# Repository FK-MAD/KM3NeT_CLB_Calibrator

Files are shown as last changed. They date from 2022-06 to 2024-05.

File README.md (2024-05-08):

# KM3NeT CLB Calibrator
## About the KM3NeT CLB Calibrator
The KM3NeT CLB Calibrator is a mechanism that automatically calibrates the magnetic compass of the central logic boards (CLBs) used in the digital optical modules (DOMs) of the [KM3NeT](https://www.km3net.org) neutrino telescope. I designed and implemented the system during my internship at [N.C.S.R. “DEMOKRITOS” - Institute of Nuclear & Particle Physics](http://www.inp.demokritos.gr) between July and September 2020.

## Motivation
Every DOM of the KM3NeT telescope is submerged near the bottom of the Mediterranean Sea and continually reports its orientation based on data from the magnetic compass located on its CLB. For the magnetic compass to work properly, a calibration routine must be carried out for every CLB before its DOM integration. Conventionally, this is done manually using a gyroscope-like tool, seen below.

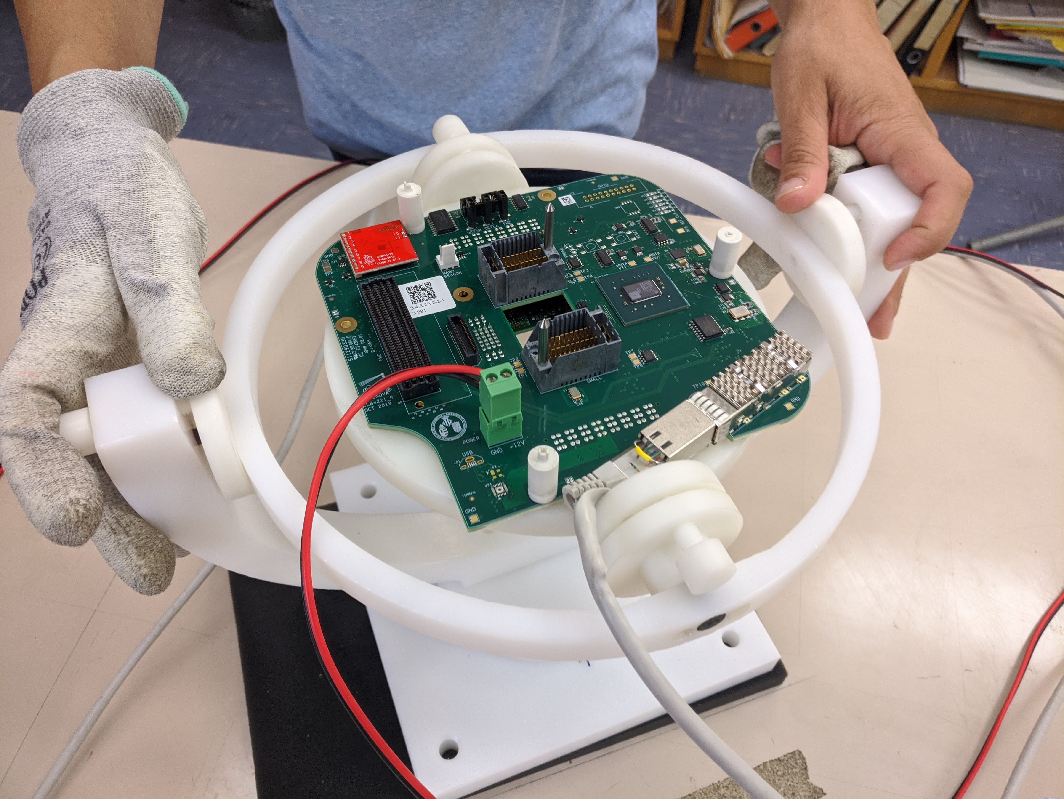
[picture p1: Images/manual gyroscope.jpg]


This process is monotonous, tedious and provides inconsistent calibration accuracy. For these reasons, an automated system needed to be developed.

## Design Constraints
The design constraints that the automated system needed to satisfy were the following.
1) No metal parts should exist near the CLB. This was to ensure that no interference occured with the earth's magnetic field during calibration.
2) The mechanism must perform a series of eight full 360° rotations about the vertical axis each one with the CLB placed in a different orientation.
3) Each rotation must be smooth and last approximately 20s to ensure good data acquisition.

## Calibrator design
The mechanism is composed of two sub-assemblies.
1) A: a gyroscope-like mechanism that rotates the CLB. It is made entirely out of plastic parts to satisfy design constraint #1. Most parts are 3D printed, some are machined in a lathe, while some are standard plastic bolts, nuts and timing belts.
2) B: a base for the stepper motors and other electronics located ~1 meter away from the CLB. Actuation between the stepper motors and the gyroscope-like mechanism is achieved using 3 long non-metalic timing belts.

Both sub-assemblies are secured on a wooden base with plastic bolts and nuts. The two sub-assemblies are seen below.



## Assembly CAD Files
The folder [Assembly Files](https://github.com/FK-MAD/KM3NeT_CLB_Calibrator/tree/main/Assembly%20Files) contains the CAD files (SolidWorks) of the automatic calibration system. Download the whole folder and open file "Calibrator Assembly v5.SLDASM".

## Electronics
Motion is achieved using three stepper motors each one controlling a rotational axis. Each motor is connected to a stepper driver on a CNC shield. Arduino UNO is used as the microcontroller and a small fan keeps the electronics cool.

## Control of Stepper Motors
Stepper motors are controled via [stepperControl.ino](Code/stepperControl.ino). To run it, the [AccelStepper](https://www.airspayce.com/mikem/arduino/AccelStepper/index.html) library must be included.

## Video
Short [video](Videos/short%20with%20CLB.mp4) (<25MB) of the calibration system performing part of the calibration routine. An old version of the mechanism in shown in the video. It has a short base, the electronics are near the CLB, and the mechanism is held in place using zip-ties.

## License
This work is licensed under a
[Creative Commons Attribution-NonCommercial-NoDerivatives 4.0 International Public License][cc-by-nc-nd].

[][cc-by-nc-nd]

[cc-by-nc-nd]: http://creativecommons.org/licenses/by-nc-nd/4.0/
[cc-by-nc-nd-image]: https://licensebuttons.net/l/by-nc-nd/4.0/88x31.png
[cc-by-nc-nd-shield]: https://img.shields.io/badge/License-CC%20BY--NC--ND%204.0-lightgrey.svg

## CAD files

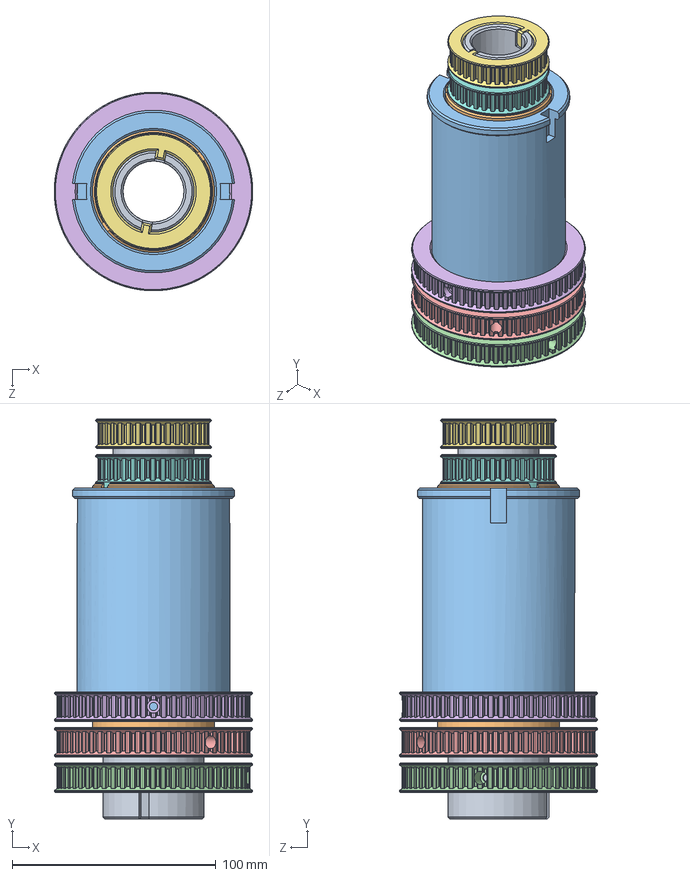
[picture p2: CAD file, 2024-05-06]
Assembly Files/tubes assembly v5.SLDASM
97.5 x 196.5 x 97.5 mm
inner tube v5
middle tube v5
outer tube v5
big inner tube pulley v5
big middle tube pulley v5
big outer tube pulley v5
small inner tube pulley v5
small middle tube pulley v5

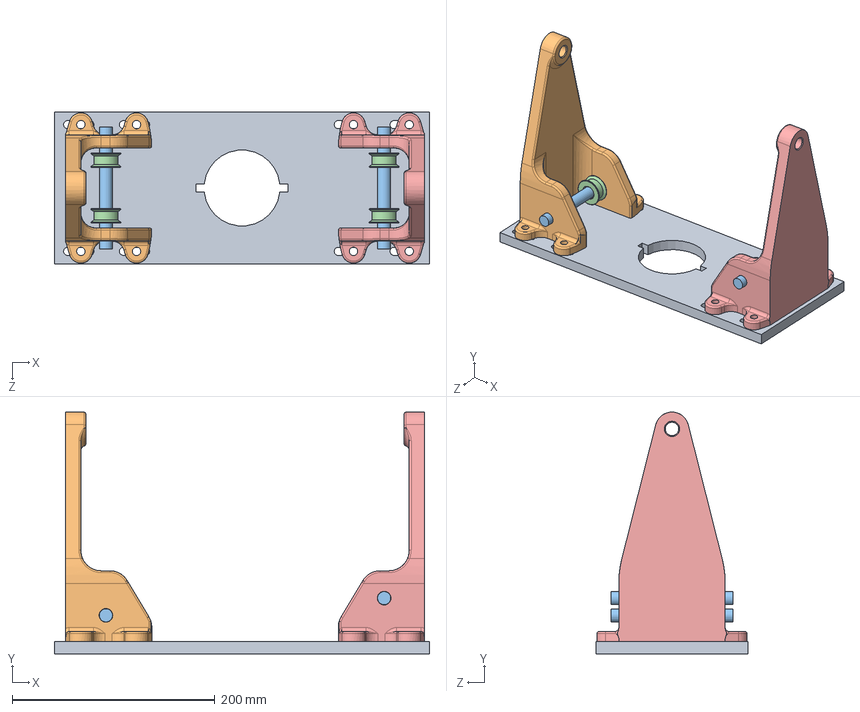
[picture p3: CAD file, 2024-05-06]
Assembly Files/outer plate assembly v5.SLDASM
370.0 x 238.5 x 150.0 mm
outer plate base v5
south outer plate pillar v5
outer plate rod v5 x 2
outer plate idler v5 x 4
north outer plate pillar v5

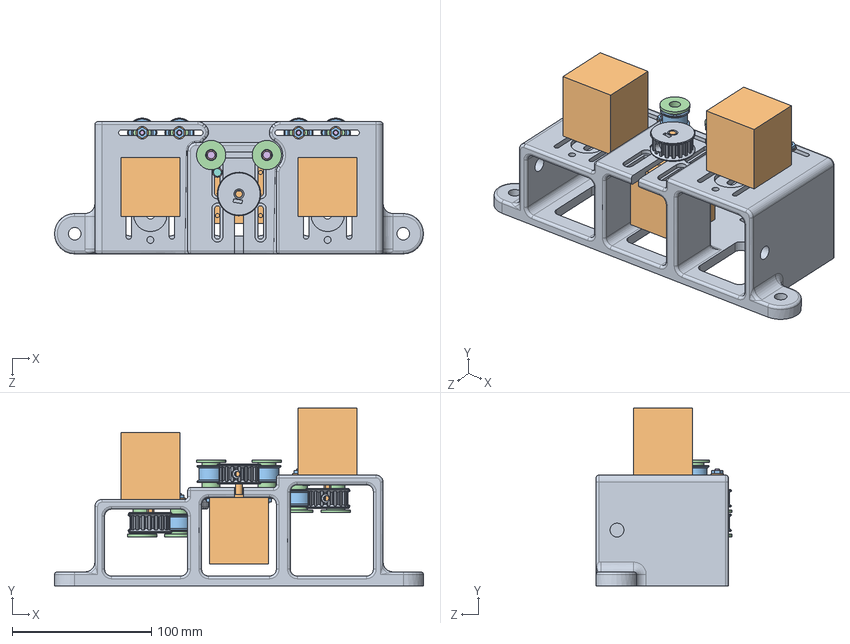
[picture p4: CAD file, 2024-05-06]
Assembly Files/stepper assembly.SLDASM
265.0 x 127.5 x 97.5 mm
stepper holder for 790
stepper x 3
belt tensioner pulley x 6
belt tensioner base x 6
M3 METAL washer x 8
M3x16 METAL bolt x 6
M3x12 METAL bolt
M3x8 METAL bolt
stepper pulley x 3
plain washer 10669 type nl_iso x 6
hex thin nut gradeb_iso x 6

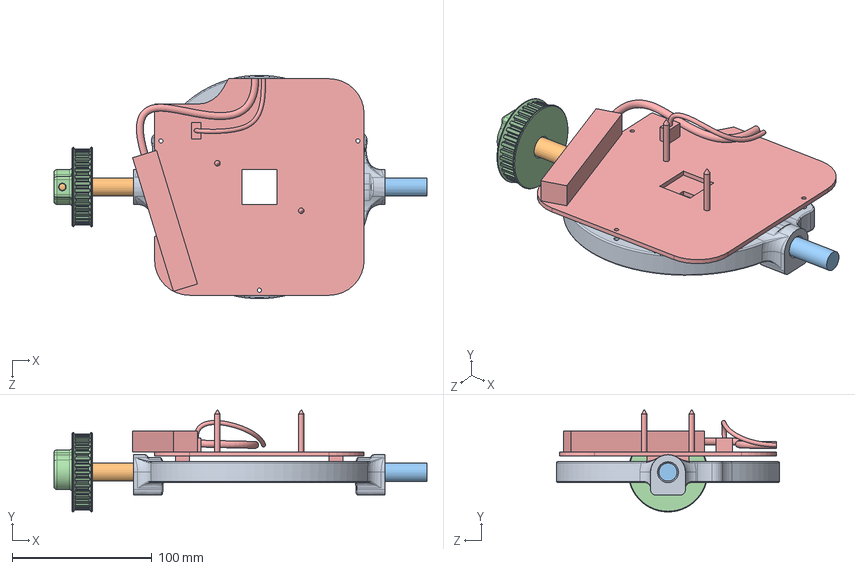
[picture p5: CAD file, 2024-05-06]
Assembly Files/inner ring assembly v5.SLDASM
267.0 x 73.0 x 159.9 mm
inner ring base v5
long inner ring arm v5
short inner ring arm v5
inner ring pulley v5
CLB
M4_nut

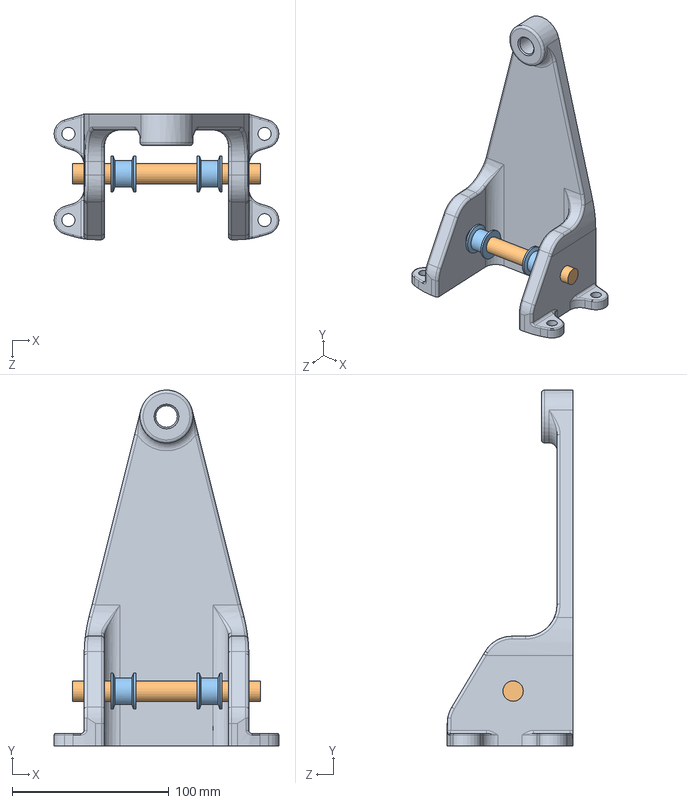
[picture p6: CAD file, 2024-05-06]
Assembly Files/south outer plate pillar assembly v5.SLDASM
143.3 x 226.9 x 80.0 mm
south outer plate pillar v5
outer plate rod v5
outer plate idler v5 x 2

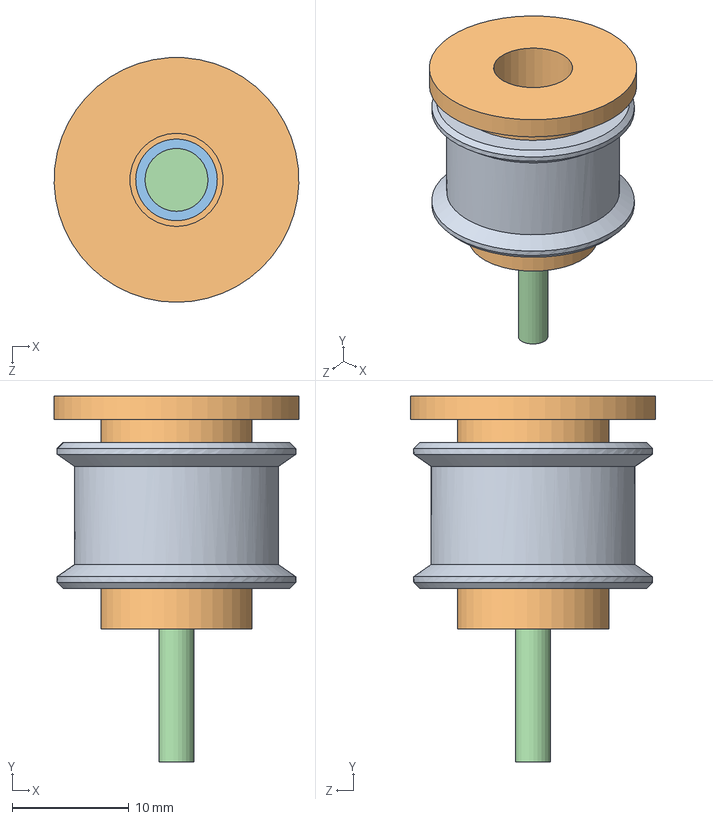
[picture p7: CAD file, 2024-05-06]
Assembly Files/belt tensioner assembly.SLDASM
21.0 x 31.4 x 21.0 mm
belt tensioner pulley
belt tensioner base
M3 METAL washer
M3x16 METAL bolt

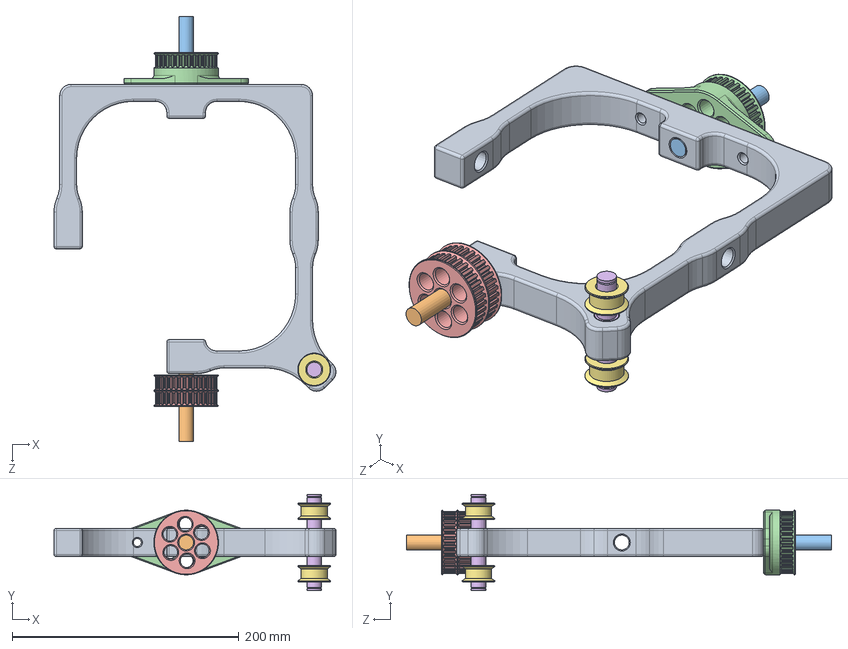
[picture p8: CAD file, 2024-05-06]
Assembly Files/middle ring assembly v5.SLDASM
248.6 x 85.0 x 375.0 mm
middle ring base v5
north middle ring arm 1 v5
south middle ring arm 1 v5
middle ring pulley 1 v5
middle ring pulley 2 v5
middle ring arm 2 v5
middle ring idler v5 x 2

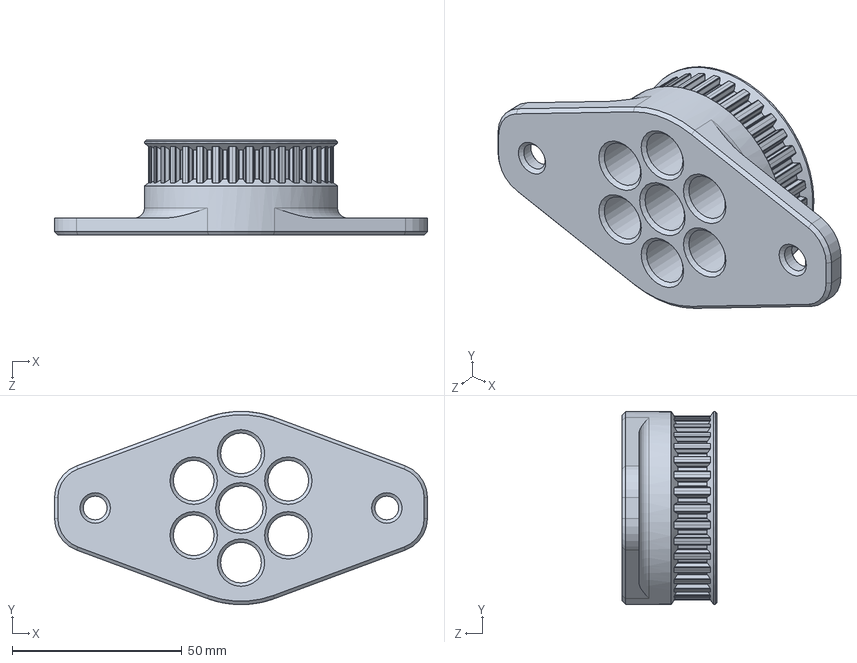
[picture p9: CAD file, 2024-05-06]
Assembly Files/middle ring pulley 1 v5.SLDPRT
110.0 x 57.0 x 28.0 mm

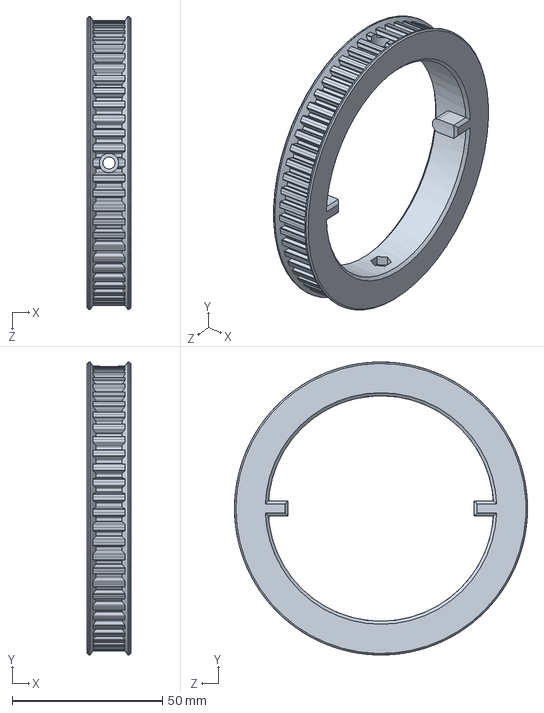
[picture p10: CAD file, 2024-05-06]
Assembly Files/big outer tube pulley v5.SLDPRT
14.5 x 97.5 x 97.5 mm

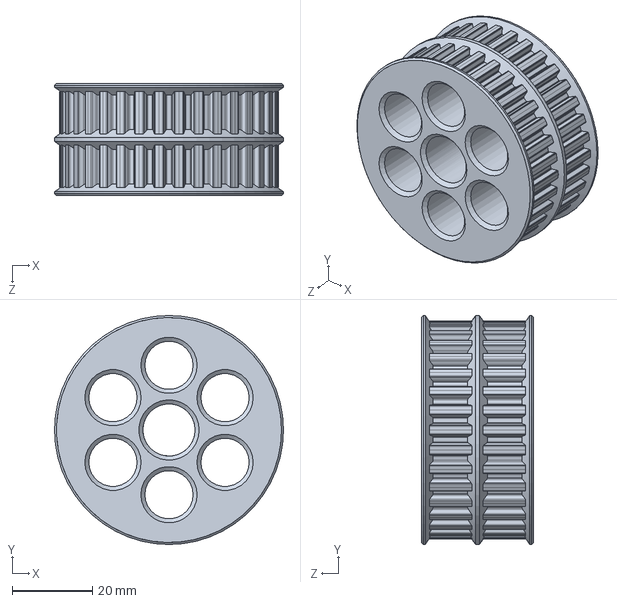
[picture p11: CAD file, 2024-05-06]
Assembly Files/middle ring pulley 2 v5.SLDPRT
57.0 x 57.0 x 28.0 mm

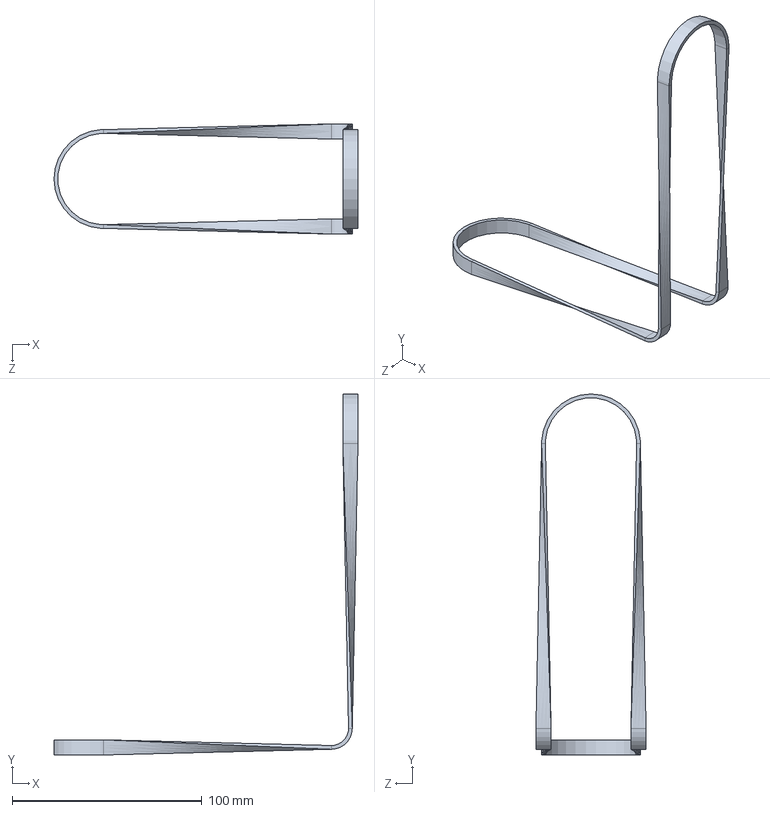
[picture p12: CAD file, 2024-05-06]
Assembly Files/belt 1.SLDPRT
160.0 x 190.0 x 58.0 mm

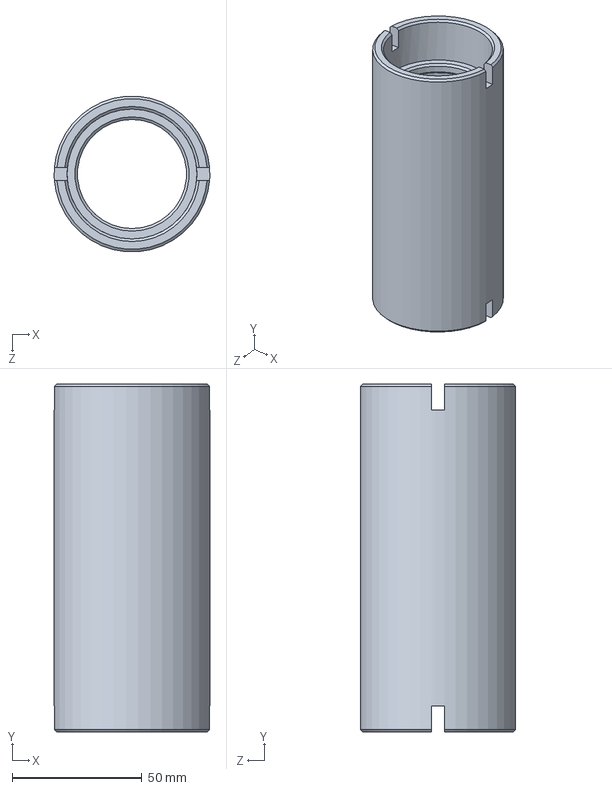
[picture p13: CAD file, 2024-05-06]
Assembly Files/middle tube v5.SLDPRT
60.0 x 134.0 x 59.8 mm

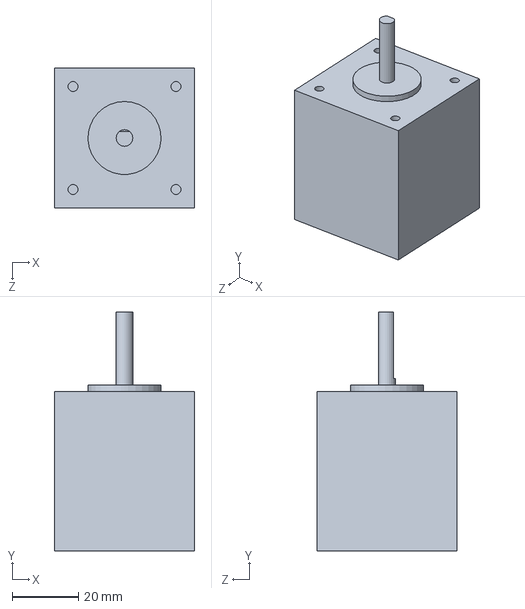
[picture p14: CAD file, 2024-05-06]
Assembly Files/stepper.SLDPRT
42.3 x 72.0 x 42.3 mm

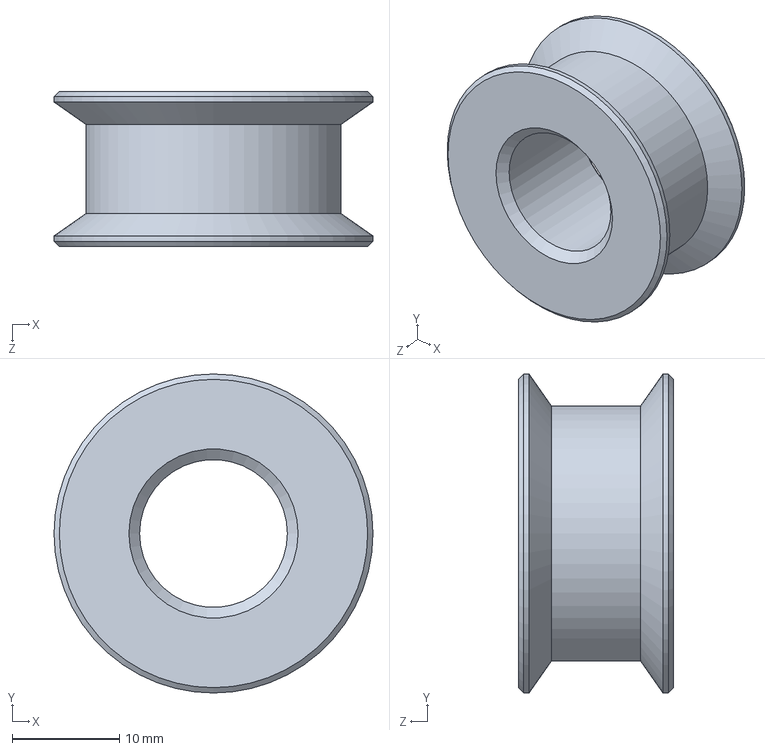
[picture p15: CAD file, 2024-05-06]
Assembly Files/outer plate idler v5.SLDPRT
29.8 x 29.8 x 14.5 mm

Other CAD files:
Assembly Files/north outer plate pillar assembly v5.SLDASM
Assembly Files/small middle tube pulley v5.SLDPRT
Assembly Files/south outer plate pillar v5.SLDPRT
Assembly Files/small inner tube pulley v5.SLDPRT
Assembly Files/M3 METAL washer.SLDPRT
Assembly Files/M3x12 METAL bolt.SLDPRT
Assembly Files/M3x16 METAL bolt.SLDPRT
Assembly Files/M3x8 METAL bolt.SLDPRT
Assembly Files/M4_bolt.SLDPRT
Assembly Files/M4_nut.SLDPRT
Assembly Files/M6_bolt.SLDPRT
Assembly Files/M6_nut.SLDPRT
Assembly Files/base_plate.SLDPRT
Assembly Files/belt 2.SLDPRT
Assembly Files/belt 3.SLDPRT
Assembly Files/belt tensioner base.SLDPRT
Assembly Files/belt tensioner pulley.SLDPRT
Assembly Files/big inner tube pulley v5.SLDPRT
Assembly Files/big middle tube pulley v5.SLDPRT
Assembly Files/cup v5.SLDPRT
Assembly Files/hex bolt gradeab_iso.sldprt
Assembly Files/hex bolt gradeb_iso.sldprt
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

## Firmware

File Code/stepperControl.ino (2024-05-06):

//----------------------------------------------------------------------------------
// This code is used to control the stepper motors of the CLB calibration mechanism.
//
// Steps to perform calibration:
// 0) Edit the "CONSTANTS" section as needed
// 1) Upload the code to the Arduino UNO
// 2) Turn on the power supply to the CNC shield
// 3) Set up the CLB with the x-axis pointing north and the z-axis pointing downwards (as per "KM3NeT_CALIB_2017_0043PRO_AHRS_Calibration_v5", page 21)
// 4) Press the pushbutton to energise the steppers and hold the CLB in position
// 5) When ready, press the pushbutton again to start the calibration
// 6) Wait for calibration to end
// 7) When ready, press the pushbutton again to start the calibration check
// 8) Wait for calibration check to end
// 9) When ready, press the pushbutton again to bring the CLB to its original position and untwist the wires
//
// Author: Filippos Katsimalis <fkatsimalis@uth.gr>, <fkatsimalis@gmail.com>
//----------------------------------------------------------------------------------


///INCLUDE THE ACCELSTEPPER LIBRARY///
#include <AccelStepper.h>


///DEFINITION OF STEP & DIRECTION PINS AND STEPPER SETUP///
// ([1],[step pin #],[direction pin #]). [1] is a declaration that a stepper driver (with Step and Direction pins) is used
AccelStepper outer(1,2,5);  // outer tube control (stepper connected to "X" on CNC shield), pin 2=step, pin 5=direction
AccelStepper middle(1,3,6); // middle tube control (stepper connected to "Y" on CNC shield), pin 3=step, pin 6=direction
AccelStepper inner(1,4,7);  // inner tube control (stepper connected to "Z" on CNC shield), pin 4=step, pin 7=direction


///CONSTANTS///
int microstep=16; // the microstep size. depends on the configuration of jumper pins used on the CNC shield, under the stepper drivers.
                  // for the stepper motor drivers used (A4988) see: https://www.pololu.com/product/1182 (step and microstep size)
                  // possible values for the A4988 are: full step -> 1. half step -> 2. quarter step -> 4. eighth step -> 8. sixteenth step -> 16

float gear_ratio=3.27778; // the gear ratio = [number of teeth of big pulleys (on the lower part of the tubes)]/[number of teeth of stepper pulleys] = 59/18

float calibration_wait_time=1;        // delay between each rotation during calibration in seconds
float calibration_check_wait_time=15; // delay between each rotation during calibration check in seconds

float yaw_time=20;             // time to perform the yaw rotation in seconds
float yaw_acceleration=100;    // acceleration/deceleration rate of yaw rotation in steps/seconds^2
float roll_time=1;             // time to perform the roll rotation in seconds
float roll_acceleration=1000;  // acceleration/deceleration rate of roll rotation in steps/seconds^2
float pitch_time=1;            // time to perform the pitch rotation in seconds
float pitch_acceleration=1000; // acceleration/deceleration rate of pitch rotation in steps/seconds^2


///CALCULATIONS///
int steps_per_rev=200*microstep;         // the number of steps required for a full revolution of a stepper axle (small pulley)
float full_rev=steps_per_rev*gear_ratio; // the number of steps required for a full revolution of a tube (big pulley) 

float yaw_speed=(1/yaw_time)*gear_ratio*steps_per_rev;     // the constant speed required to perform a yaw rotation in the specified time in steps/seconds
float roll_speed=(1/roll_time)*gear_ratio*steps_per_rev;   // the constant speed required to perform a roll rotation in the specified time in steps/seconds
float pitch_speed=(1/pitch_time)*gear_ratio*steps_per_rev; // the constant speed required to perform a pitch rotation in the specified time in steps/seconds


void setup() {

  
  ///PIN DEFINITION AS OUTPUT///
  pinMode(2, OUTPUT);
  pinMode(5, OUTPUT);
  pinMode(3, OUTPUT);
  pinMode(6, OUTPUT);
  pinMode(4, OUTPUT);
  pinMode(7, OUTPUT);
  pinMode(8, OUTPUT);
  pinMode(9, OUTPUT);


  ///WAIT UNTIL CLB IS READY TO BE CALIBRATED///
  // pin 8=enable. HIGH -> steppers are disabled. LOW -> steppers are enabled
  digitalWrite(8,HIGH); // disable steppers
  while (digitalRead(9) == HIGH) {
  // do nothing. wait until the user levels the CLB and points it towards north. when the pushbutton is pressed the code exits the loop and the steppers are energised.
  }
  digitalWrite(8,LOW); // enable steppers
  while (digitalRead(9) == HIGH) {
  // do nothing. wait until calibration is ready to begin. when the pushbutton is pressed the code exits the loop and calibration starts.
  }
  
  ///SEQUENCE OF ROTATIONS///
  // yaw->rotation around the z-axis, pitch->rotation around the x-axis, roll->rotation around the y-axis
  // axes of the CLB are shown on "KM3NeT_CALIB_2017_0043PRO_AHRS_Calibration_v5", page 5
  // yaw rotations are alternating in direction to not twist the cables
  // full_rev=360 deg, full_rev/4=90 deg, full_rev/8=45 deg


  ///CALIBRATION///
  // roll rotations
  yaw(full_rev);
    roll(full_rev/4);
  yaw(-full_rev);
    roll(full_rev/4);  
  yaw(full_rev);
    roll(-3*full_rev/4); 
  yaw(-full_rev);
    roll(full_rev/4);

  // pitch rotations
    pitch(full_rev/4);
  yaw(full_rev);
    pitch(-full_rev/2);
  yaw(-full_rev);
    pitch(full_rev/4);
  
  // inclined (roll & pitch) rotations 
    roll(full_rev/8);
  yaw(full_rev);
    pitch(full_rev/8);
  yaw(-full_rev);
    roll(-full_rev/8);
  pitch(-full_rev/8);

  // end of calibration

  while (digitalRead(9) == HIGH) {
  // do nothing. wait until calibration check is ready to begin. when the pushbutton is pressed the code exits the loop and calibration check starts.
  }

  ///CALIBRATION CHECK///
  // yaw rotations
  yaw(full_rev/4);
    delay(calibration_check_wait_time*1000);
  yaw(full_rev/4);
    delay(calibration_check_wait_time*1000);  
  yaw(full_rev/4);

  // end of calibration check

  while (digitalRead(9) == HIGH) {
  // do nothing. when the pushbutton is pressed the code exits the loop and the CLB comes to its original position in order to keep the wires twist-free. 
  }

  ///CLB TO ITS ORIGINAL POSITION IN ORDER TO KEEP THE WIRES TWIST-FREE///
  // yaw rotations
  yaw(-3*full_rev/4);

  // end of sequence
 
}


void loop() {} // there is no need for the "loop()" function


///YAW FUNCTION///
// all motors are needed (outer, middle and inner)
void yaw(int x){
  outer.setMaxSpeed(yaw_speed);
  outer.setAcceleration(yaw_acceleration);
  outer.moveTo(x);
  middle.setMaxSpeed(yaw_speed);
  middle.setAcceleration(yaw_acceleration);
  middle.moveTo(-x);
  inner.setMaxSpeed(yaw_speed);
  inner.setAcceleration(yaw_acceleration);
  inner.moveTo(-x);

  while (outer.run() == true) {
    outer.run();
    middle.run();
    inner.run();
  }

  outer.setCurrentPosition(0);
  middle.setCurrentPosition(0);
  inner.setCurrentPosition(0);

  delay(calibration_wait_time*1000);
}


///ROLL FUNCTION///
// middle and inner motors are needed
void roll(int y){
  middle.setMaxSpeed(roll_speed);
  middle.setAcceleration(roll_acceleration);
  middle.moveTo(y);
  inner.setMaxSpeed(roll_speed);
  inner.setAcceleration(roll_acceleration);
  inner.moveTo(-y);

  while (middle.run() == true) {
    middle.run();
    inner.run();
  }

  middle.setCurrentPosition(0);
  inner.setCurrentPosition(0);

  delay(calibration_wait_time*1000);
}


///PITCH FUNCTION///
// only inner motor is needed
void pitch(int z){
  inner.setMaxSpeed(pitch_speed);
  inner.setAcceleration(pitch_acceleration);
  inner.moveTo(z);

  while (inner.run() == true) {
    inner.run();
  }

  inner.setCurrentPosition(0);

  delay(calibration_wait_time*1000);
}
